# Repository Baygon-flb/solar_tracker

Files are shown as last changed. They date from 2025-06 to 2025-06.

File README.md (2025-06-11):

# solar_tracker
## Seguidor solar

Este projeto implementa um experimento de um seguidor que localiza uma fonte de luz e
mantém um sensor RGB apontado perpendicularmente para esta fonte, utilizando um arduíno Nano
como controlador. 

O objetivo é fazer a medição das intensidades dos componentes expectrais cromáticos RGB da luz 
solar ao longo de um dia, a partir do que é possível também calcular a temperatura de cor e a
intensidade total. 

Para essa medição é utilizado um módulo TCS34725 RGB Light Sensor.

O projeto conta com dois servos motores, um que controla a coordenada de altura e outro a 
coordenada de azimute do sensor, além de 4 LDR's, dispostos nas extremidades da placa de 
suporte do sensor, posicionados nos quadrantes presumidos como os pontos cardeais N,S,L e O. 

Com base na diferença de leitura dos LDR's, os motores são acionados, reposicionando a placa de
suporte do sensor, objetivando reorientar o conjunto até que haja convergência nos valores lidos 
dos LDR's (todos recebendo a mesma quantidade de luz), dentro de uma margem de erro estipulada, 
garantindo assim que o sensor estará, o máximo possível, apontado de forma perpendicular à fonte 
de luz. 

A leitura dos dados do sensor é realizada em um intervalo definido de tempo. Essas leituras são 
armazenadas na memória EEprom do arduíno e depois baixadas, via conexão serial, para um terminal, 
afim de que possam ser então capturados e tratados. Para controlar o intervalo de coleta dos 
dados do sensor é utilizado um módulo RTC (DS1307).

Os servos são controlados (sem uso de bilbioteca) através de uma rotina de timer interrupt, afim 
de garantir que não ocorrerão flickers ou jammers que comprometam a estabilidade da posição do 
sensor.

O detalhamento completo da elaboração e construção do projeto pode ser encontrado na pasta de 
documentação (pasta DOC).

Os componentes utilizados no projeto são:

* Arduino nano V3
* Módulo sensor TCS34725
* Módulo RTC DS1307
* Módulo StepDown DC/DC LM2596

As pastas do projeto são:
* CAD - Desenhos DWG dos componentes de montagem da caixa e suportes
* KICAD - Esquemático eletrônico e PCB
* INO - Arquivos de Sketch para a IDE do arduino
* STL - Arquivos para impressão das partes dos componentes de montagem
* DOC - Documentação do projeto

@baygon-flb

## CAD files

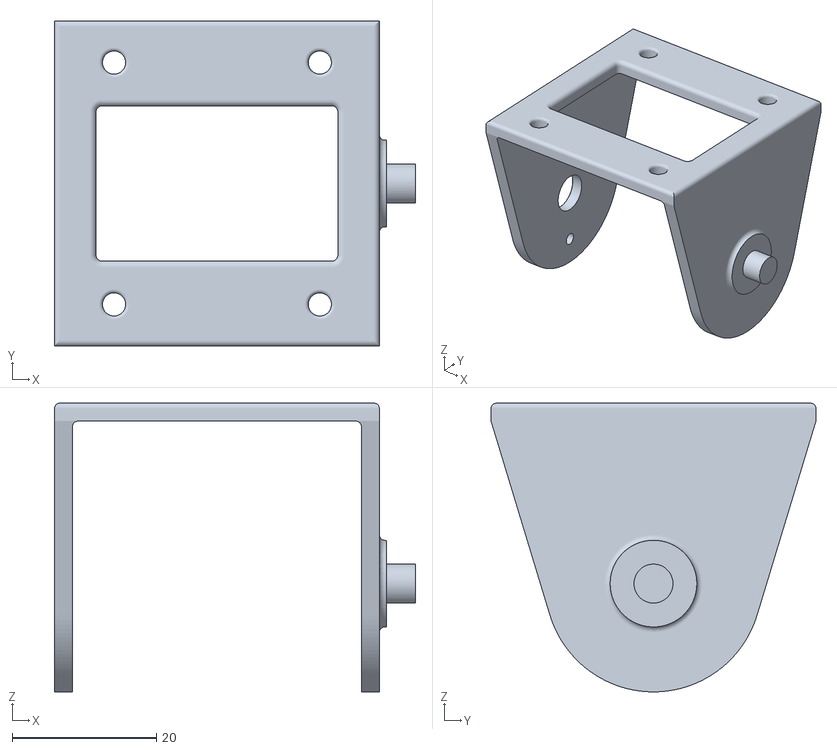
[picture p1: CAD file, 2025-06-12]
stl/suporte.stl
50.0 x 45.0 x 40.0

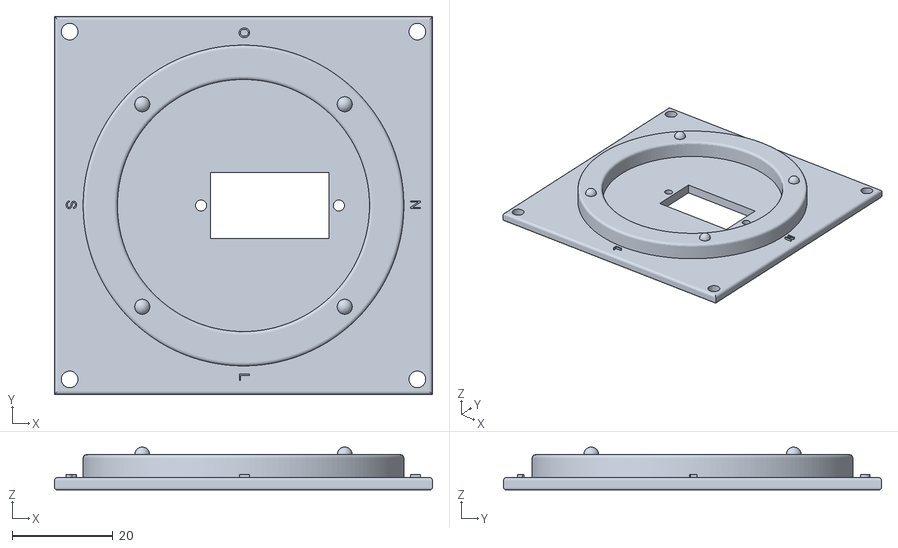
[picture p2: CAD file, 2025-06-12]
stl/tampa.stl
75.0 x 75.0 x 8.50

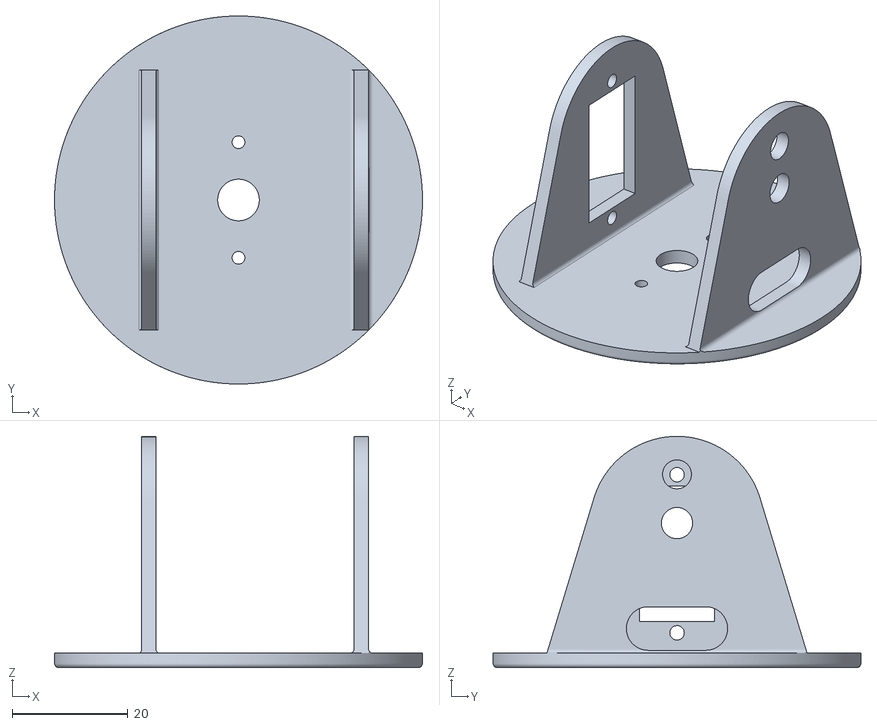
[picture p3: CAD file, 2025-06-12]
stl/base.stl
63.6 x 63.6 x 40.0

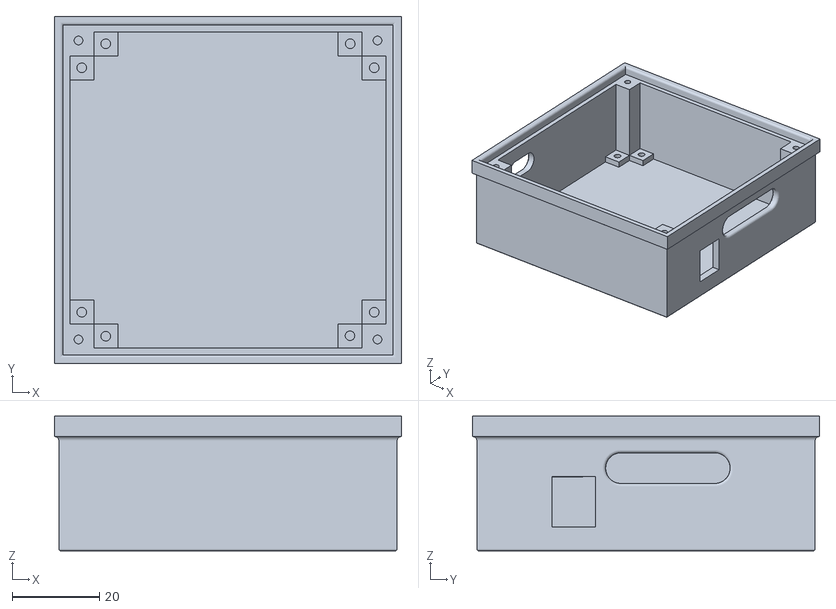
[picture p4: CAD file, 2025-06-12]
stl/caixa.stl
79.5 x 79.5 x 30.9

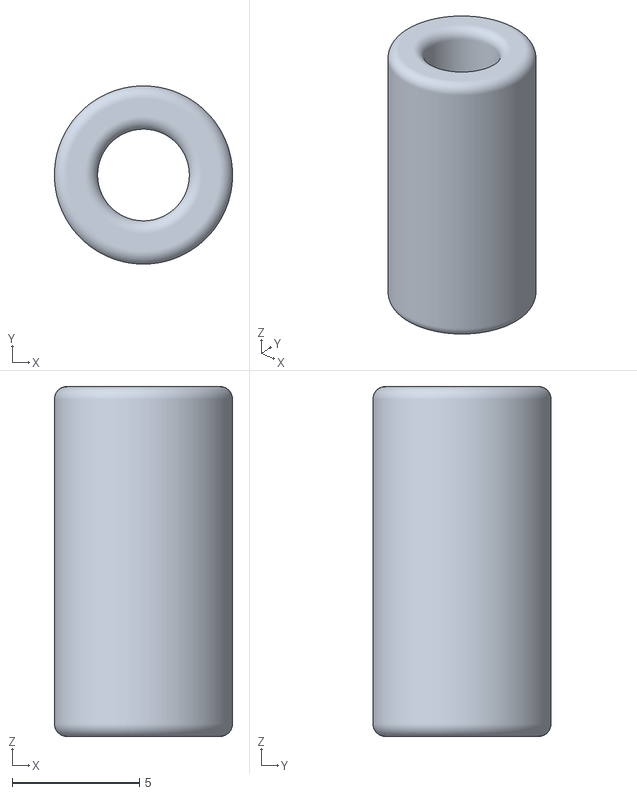
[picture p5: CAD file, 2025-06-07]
stl/espacador2.stl
7.00 x 7.00 x 13.8

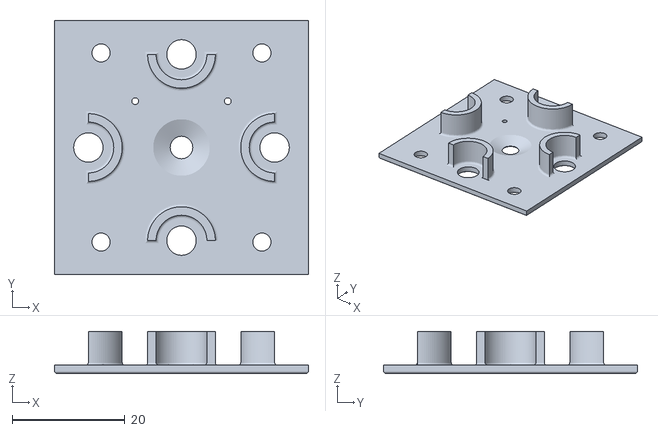
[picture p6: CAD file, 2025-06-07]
stl/pl_sensor.stl
45.0 x 45.0 x 7.50

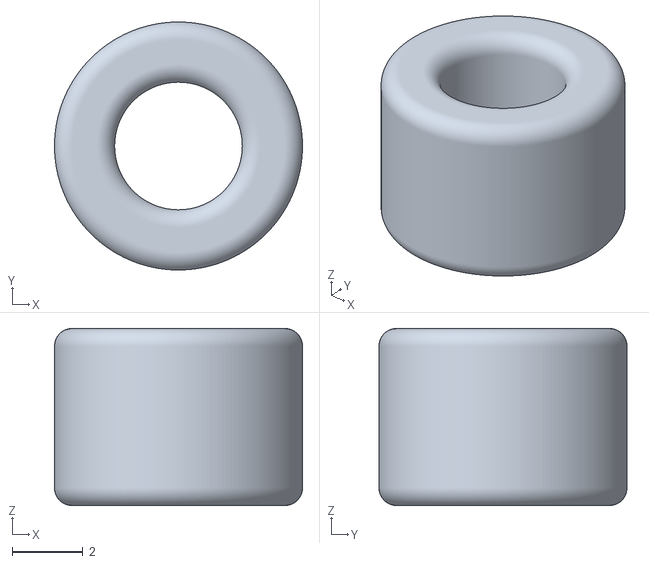
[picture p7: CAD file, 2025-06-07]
stl/espacador1.stl
7.00 x 7.00 x 5.00

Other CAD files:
cad/solar_tracker.dwg

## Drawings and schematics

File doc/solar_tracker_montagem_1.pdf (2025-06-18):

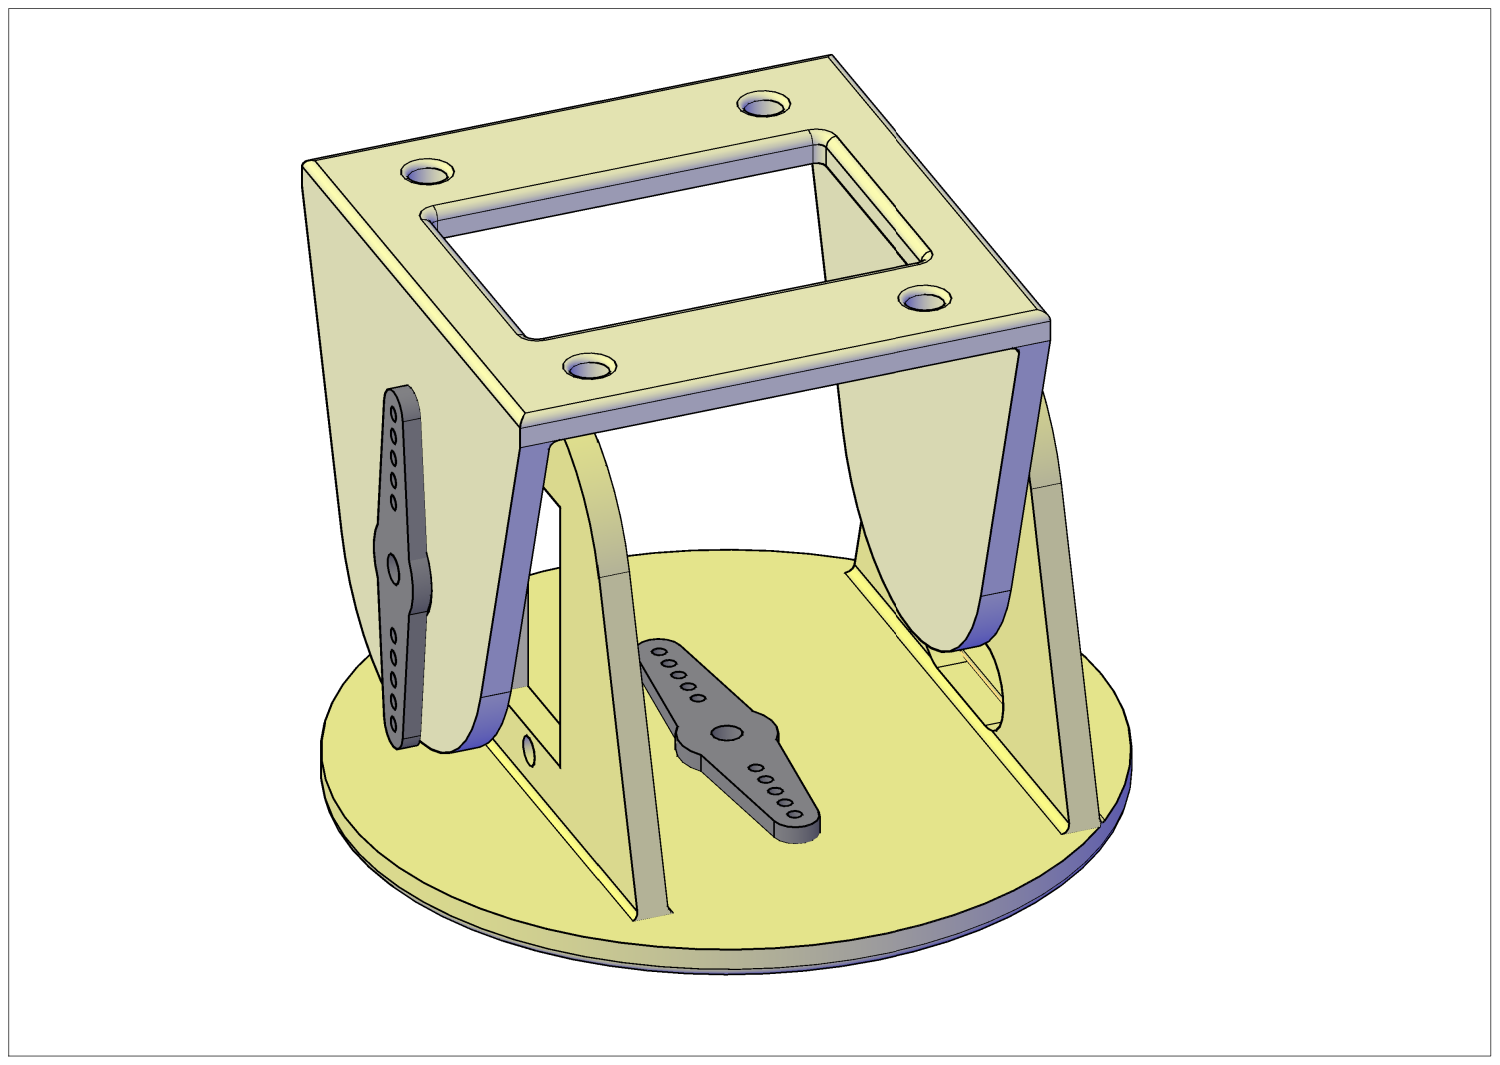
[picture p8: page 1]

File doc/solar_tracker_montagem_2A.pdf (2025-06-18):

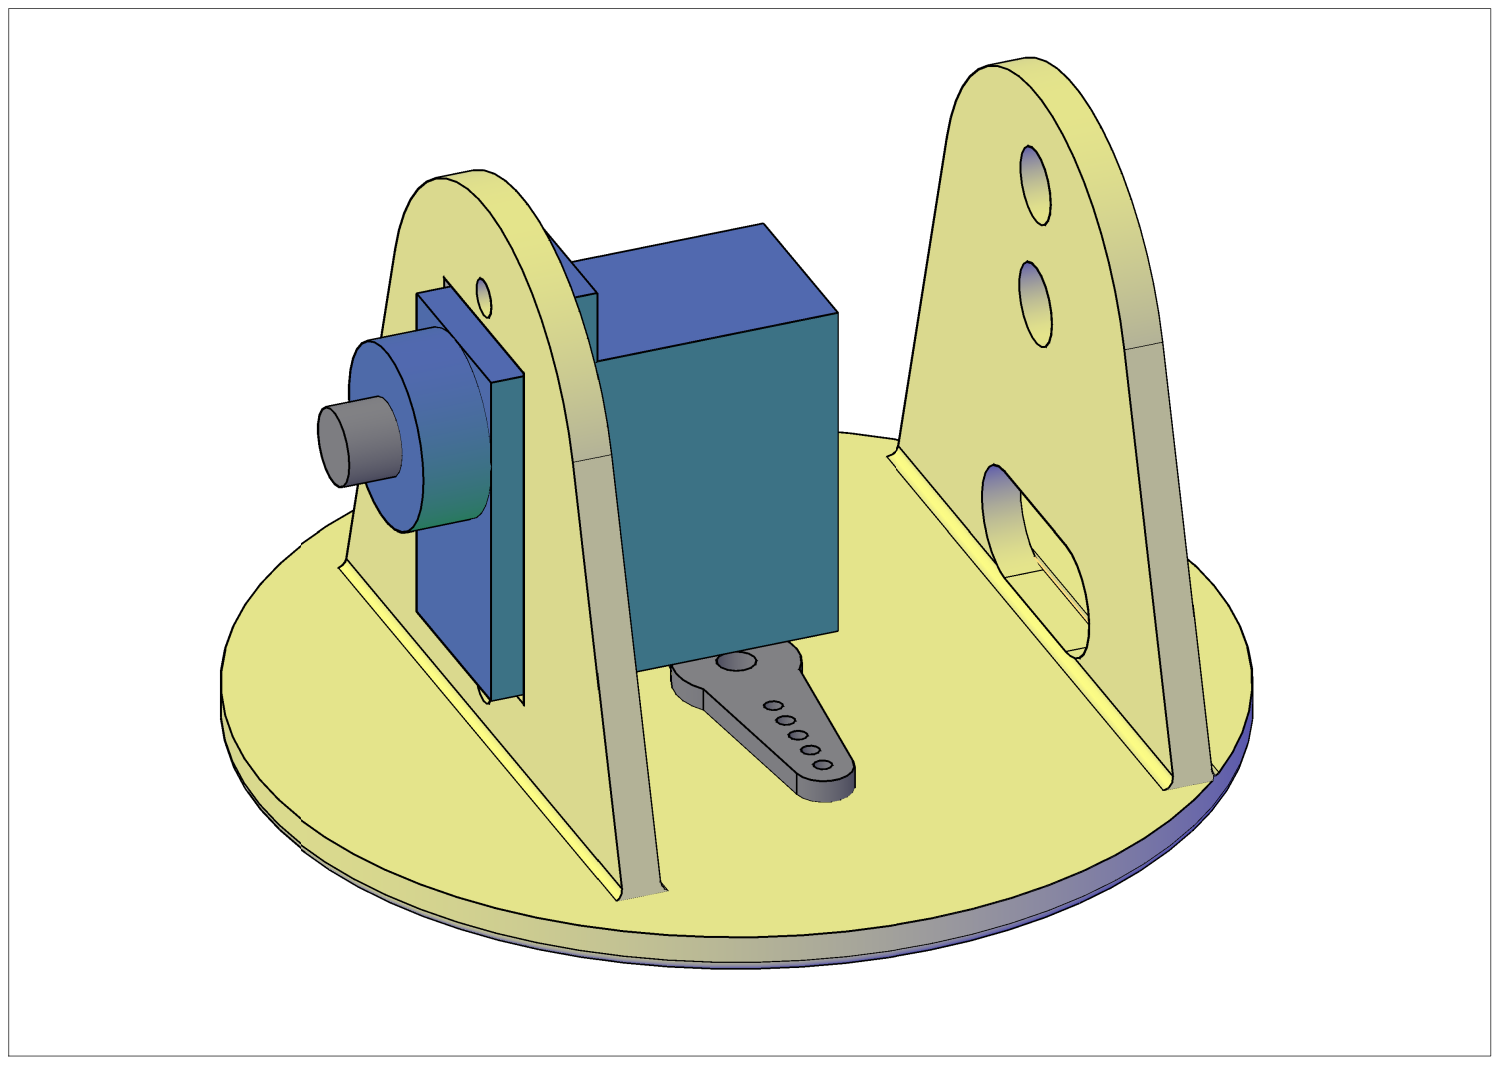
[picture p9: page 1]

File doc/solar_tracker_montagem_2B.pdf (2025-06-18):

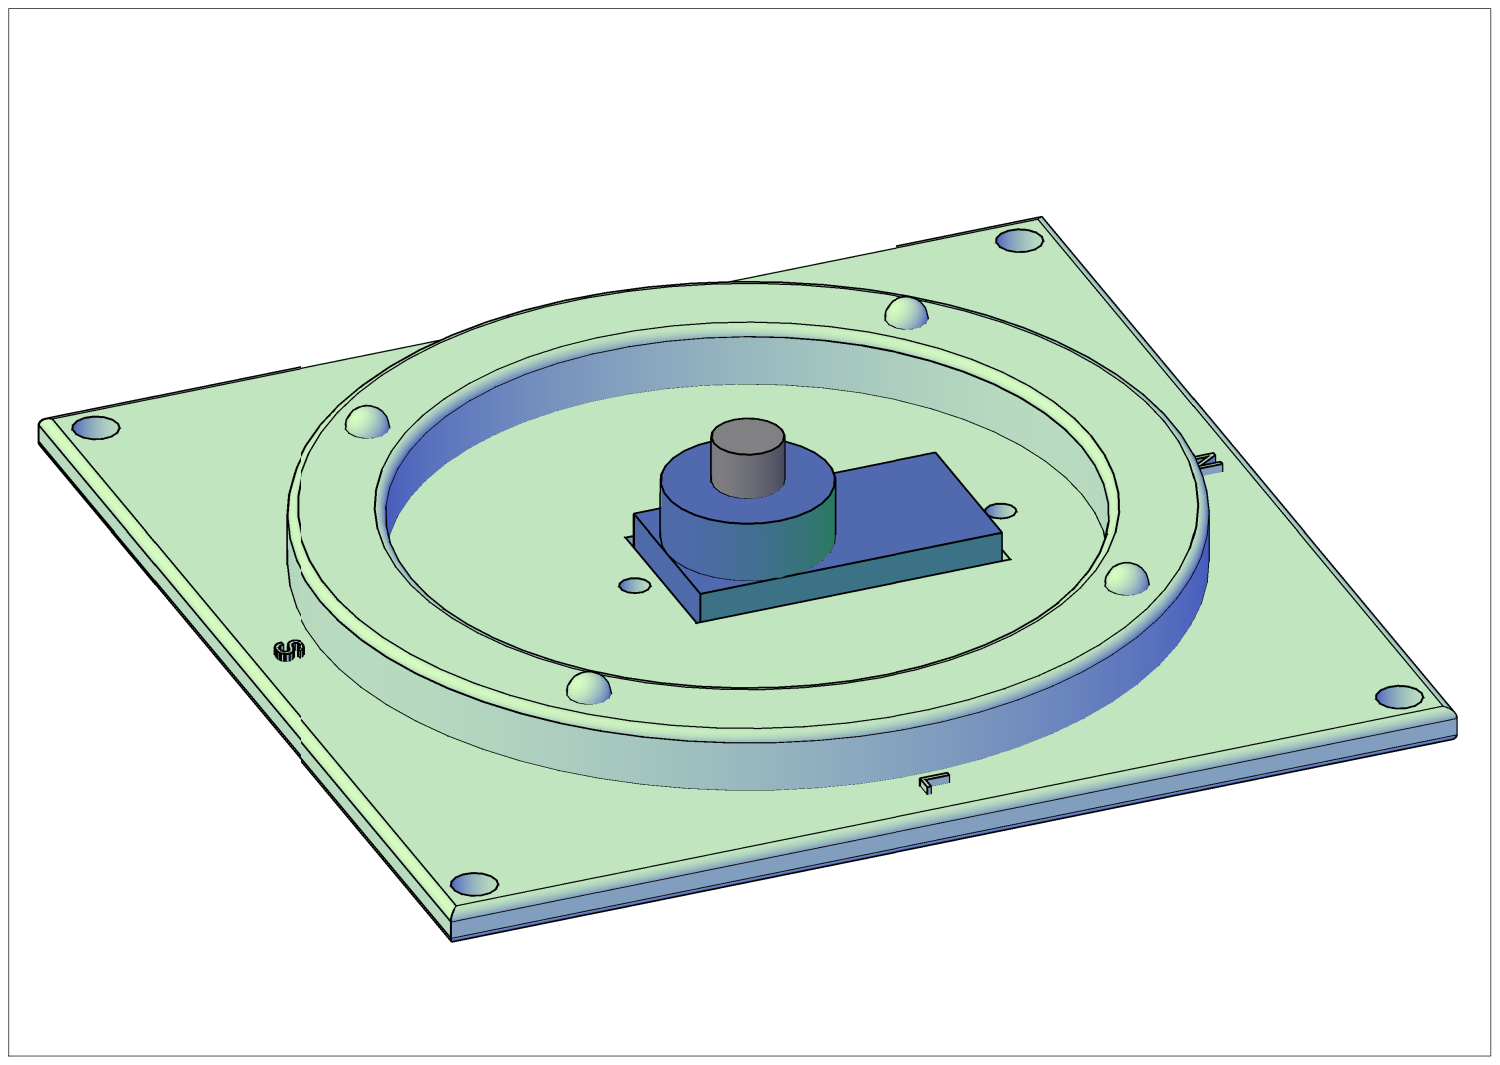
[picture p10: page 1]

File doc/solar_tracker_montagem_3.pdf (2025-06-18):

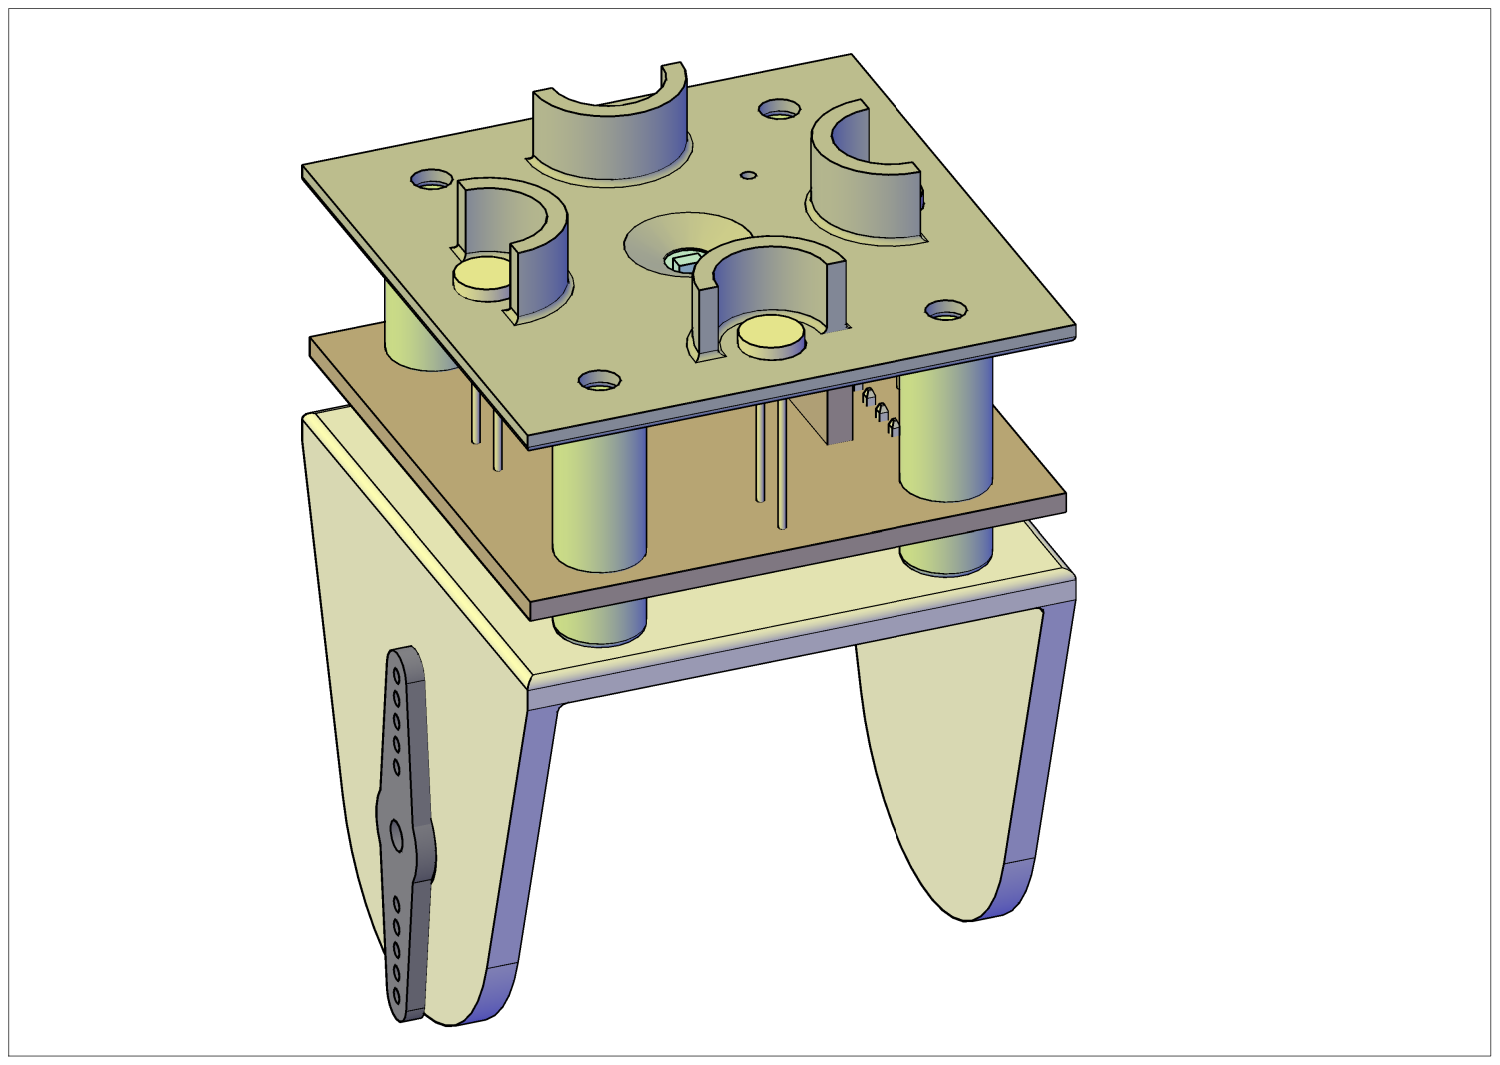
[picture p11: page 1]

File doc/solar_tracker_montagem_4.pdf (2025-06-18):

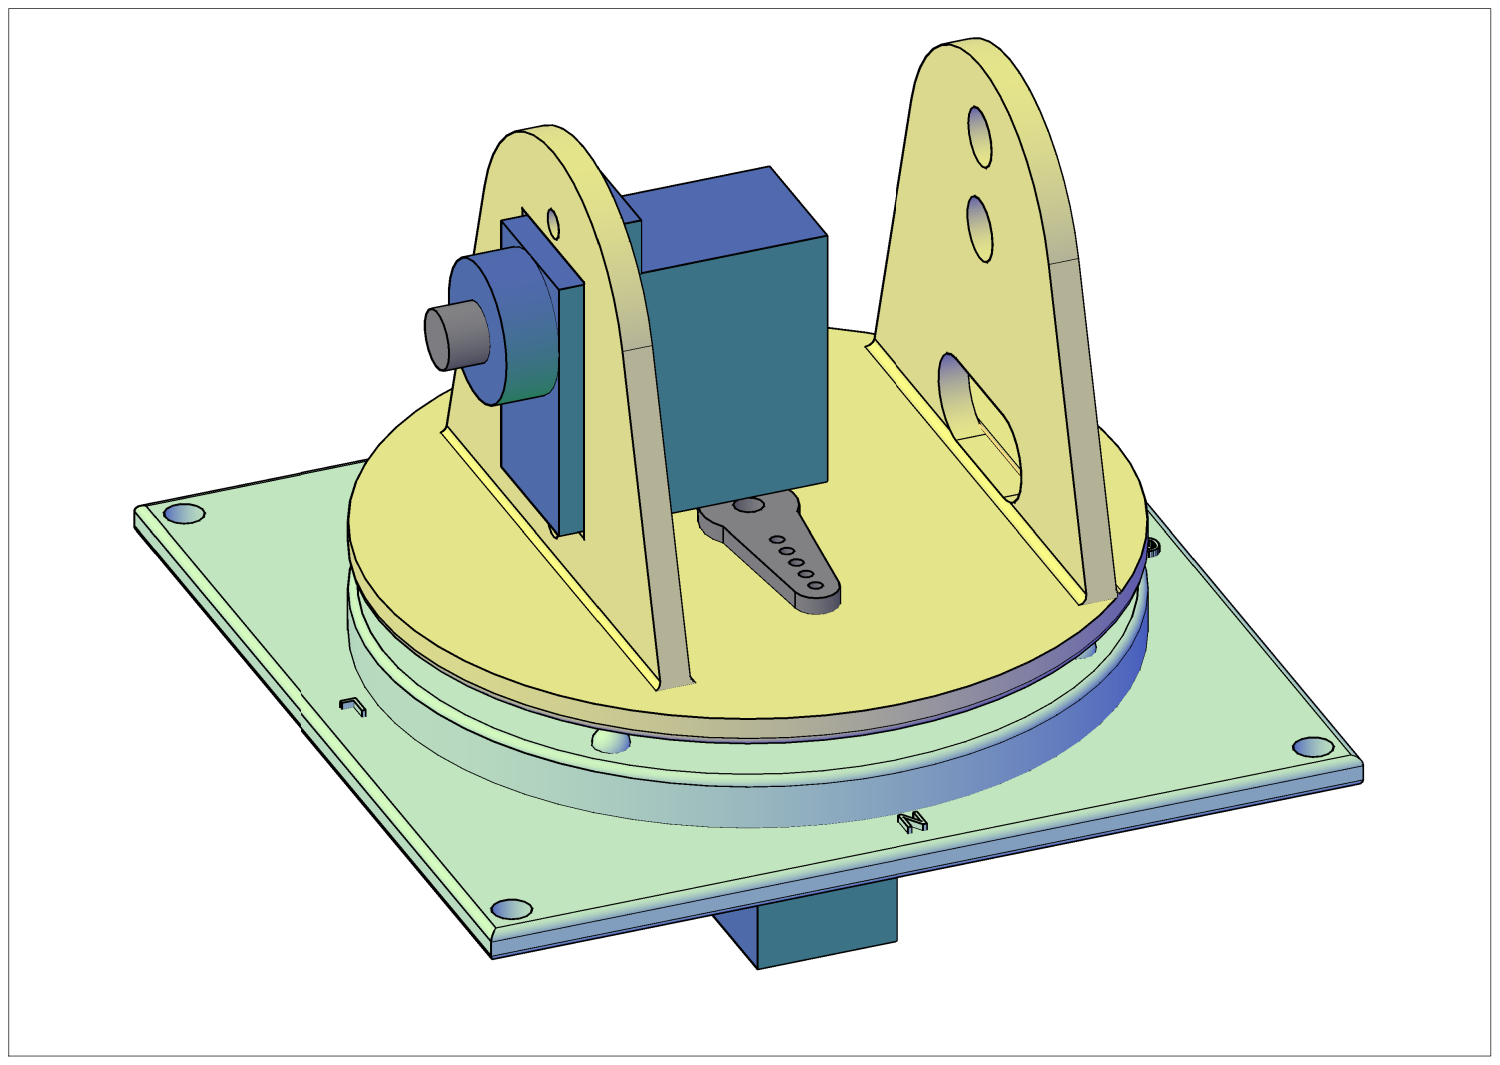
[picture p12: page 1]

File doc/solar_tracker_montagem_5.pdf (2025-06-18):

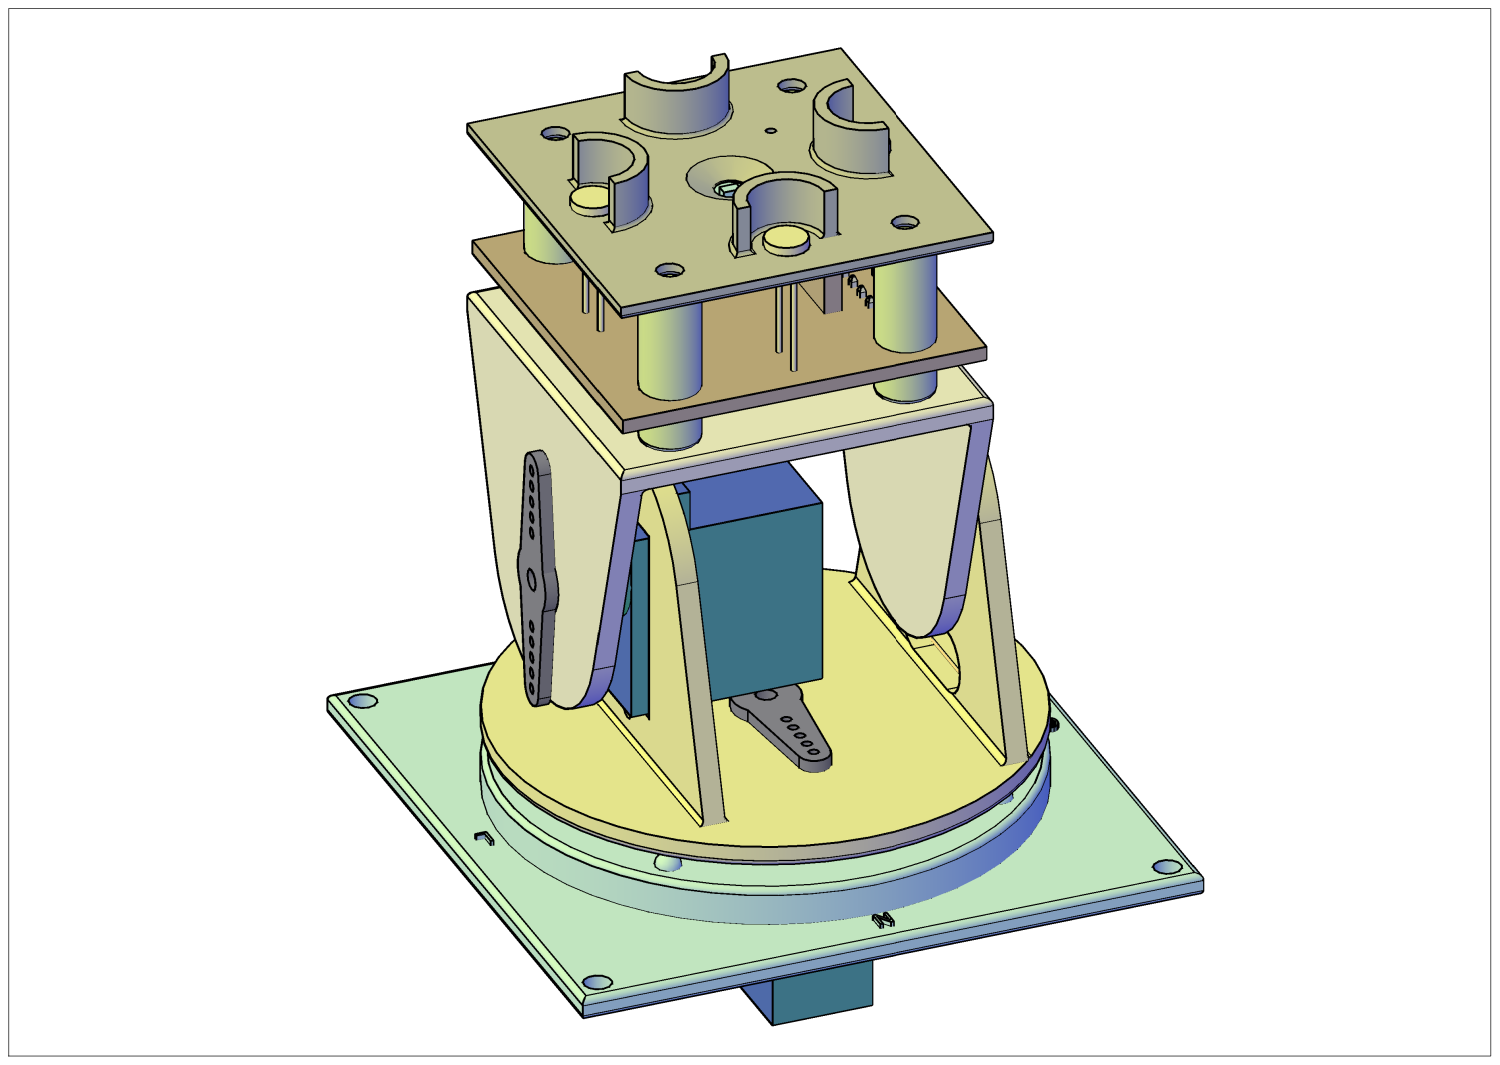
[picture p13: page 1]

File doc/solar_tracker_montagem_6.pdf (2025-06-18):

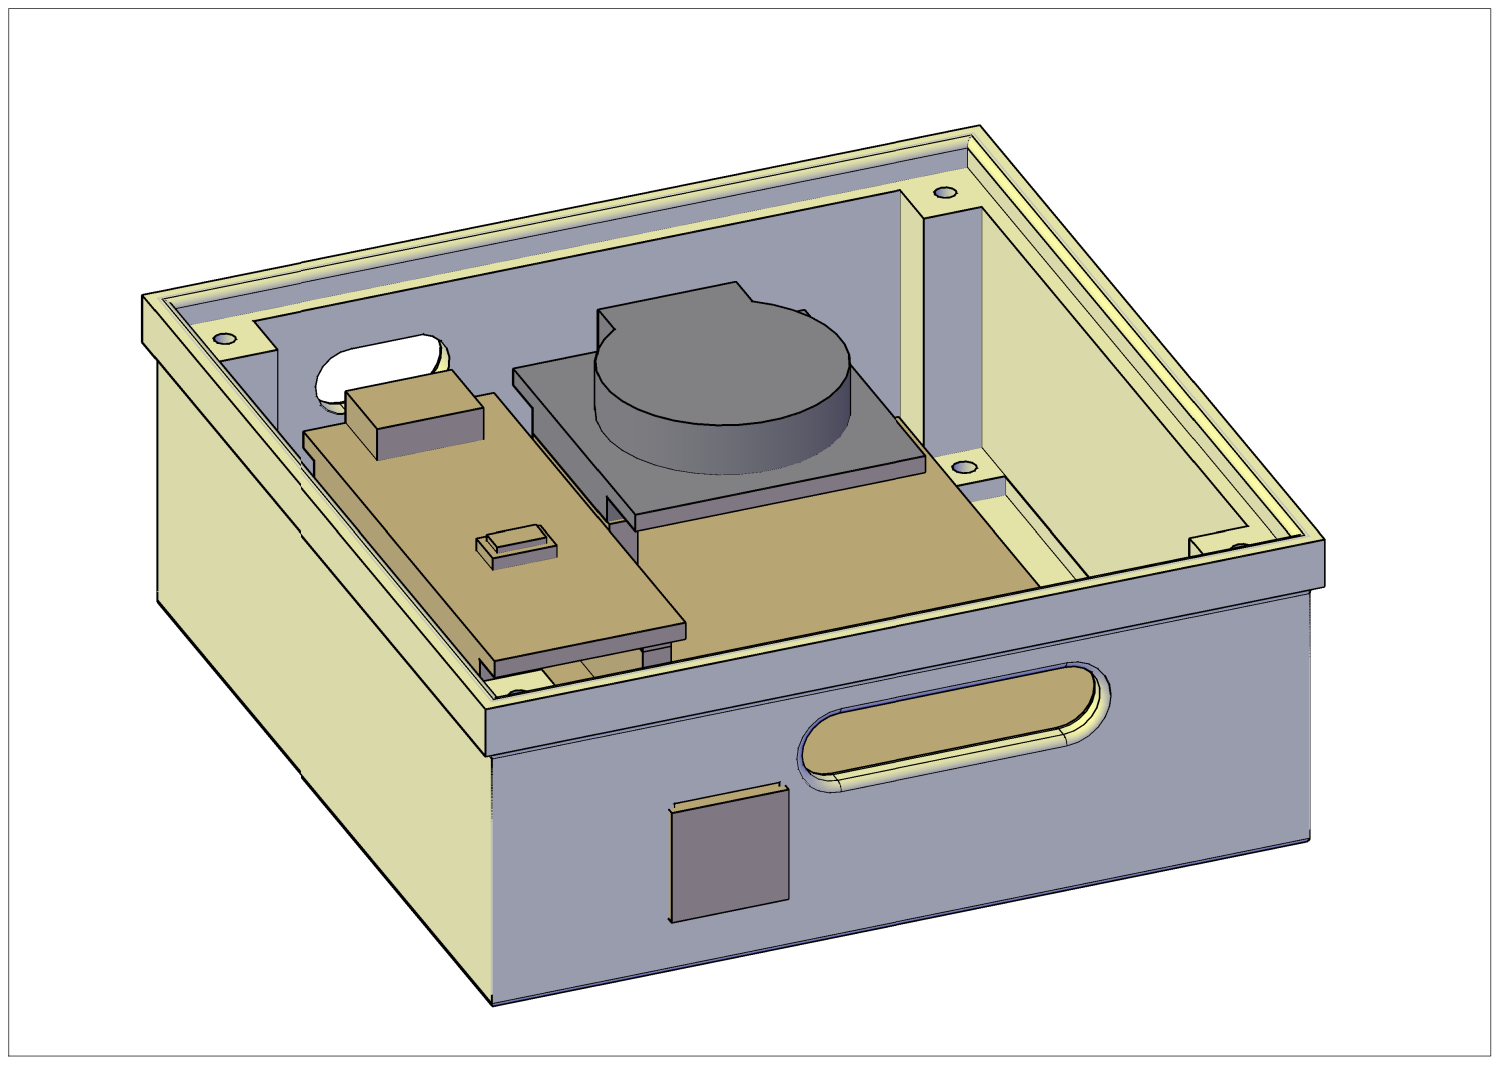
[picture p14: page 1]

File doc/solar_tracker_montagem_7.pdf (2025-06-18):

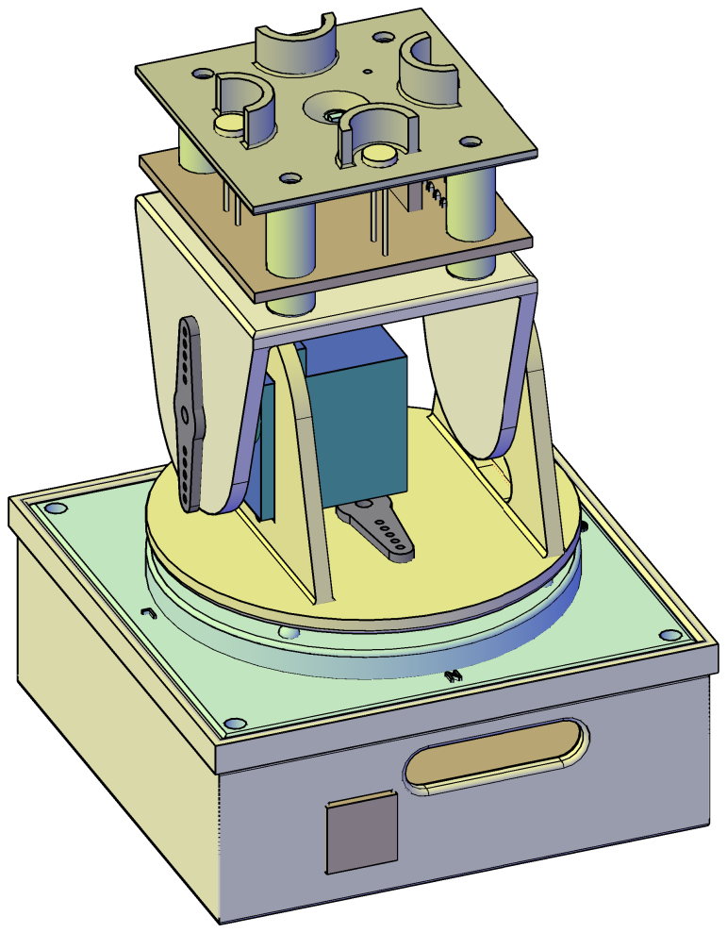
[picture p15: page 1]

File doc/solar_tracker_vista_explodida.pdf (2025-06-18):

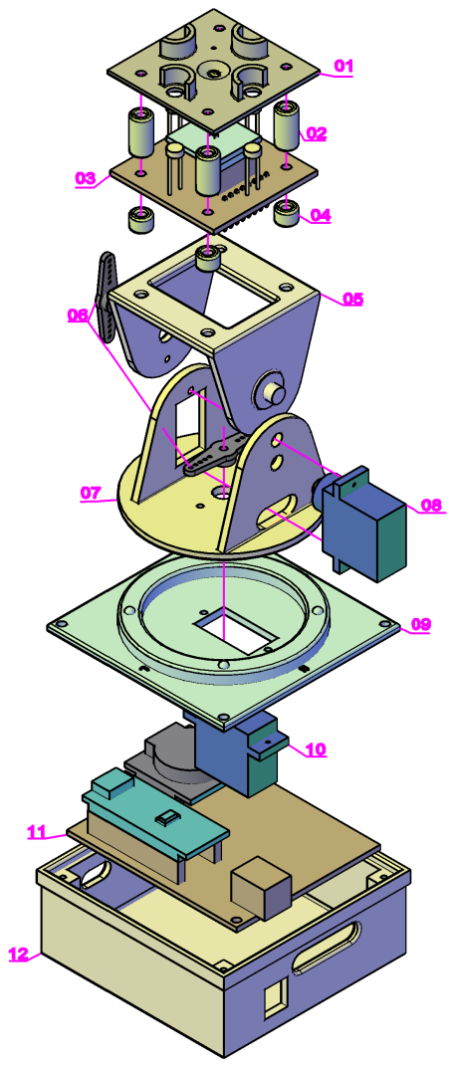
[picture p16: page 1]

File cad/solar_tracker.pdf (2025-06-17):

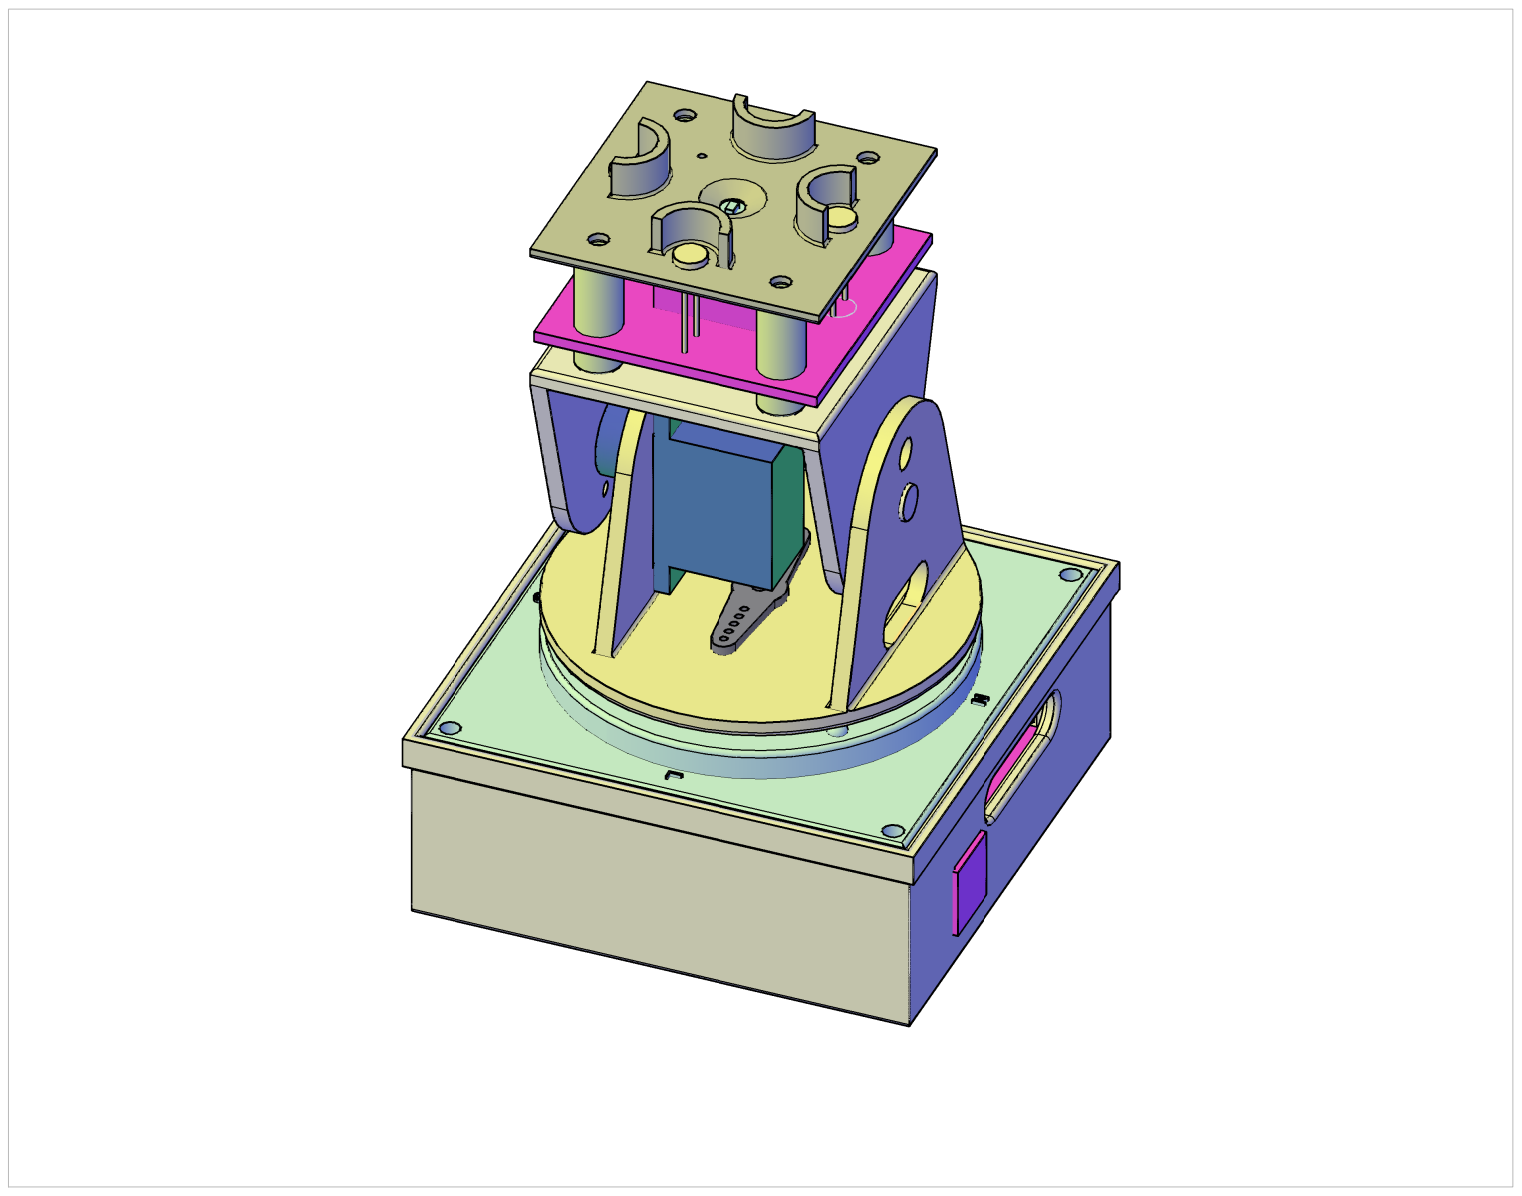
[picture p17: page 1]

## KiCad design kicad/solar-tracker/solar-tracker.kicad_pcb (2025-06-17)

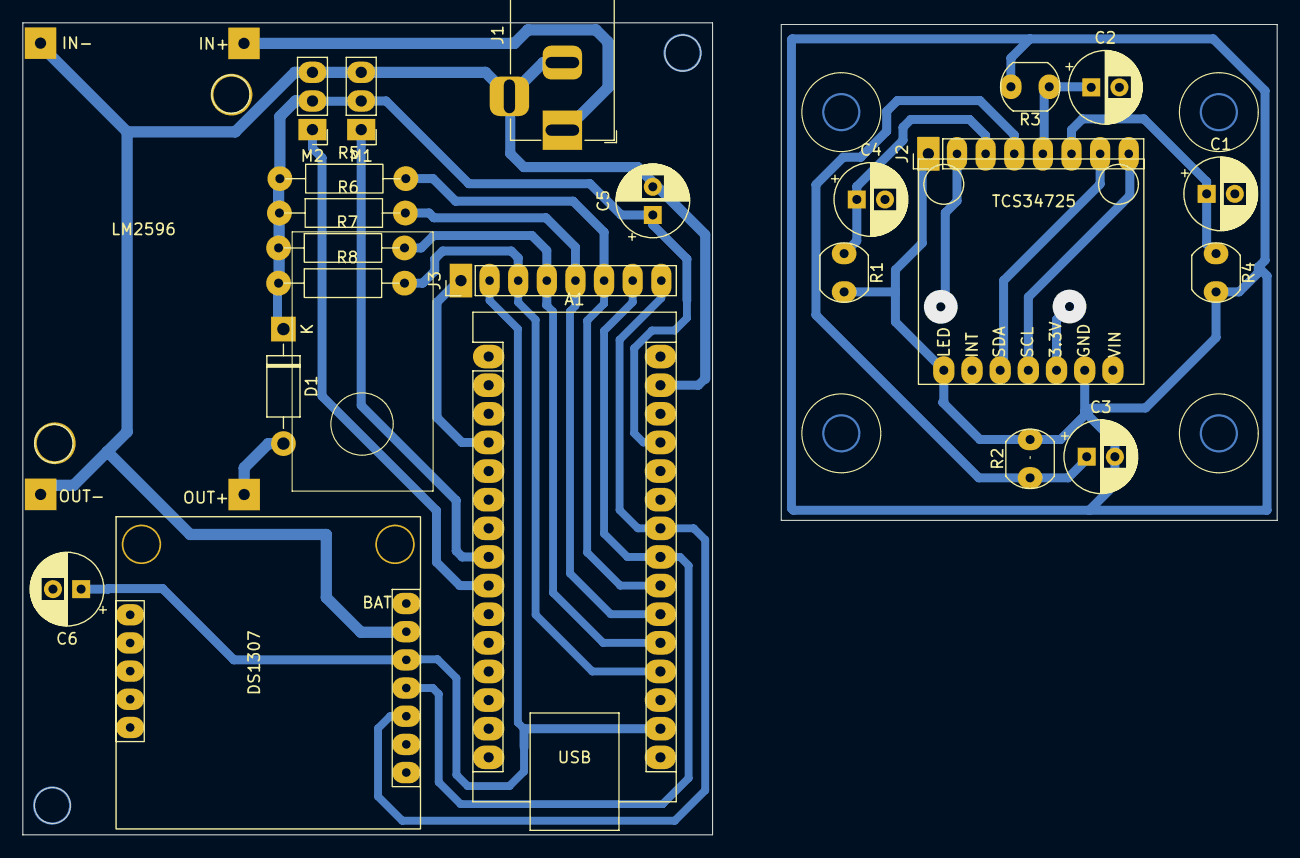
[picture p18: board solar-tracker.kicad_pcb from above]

Board: 2 copper layers, 111.3 x 72.0 mm, 24 parts (0 on the bottom side), 13 nets.

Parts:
A1: Arduino_Nano_v3.x; Arduino_Nano
C1, C2, C3, C4: 1uf; CP_Radial_D6.3mm_P2.50mm
C5, C6: 100UF; CP_Radial_D6.3mm_P2.50mm
D1: 1N4007; D_DO-41_SOD81_P10.16mm_Horizontal
DS1307: DS1307_RTC_MODULE
J1: Barrel_Jack_Switch; BarrelJack_Horizontal
J2, J3: Conn_01x08_Pin; PinHeader_1x08_P2.54mm_Vertical_large_pad
LM2596: LM2596_Step_Down_module
M1, M2: Motor_Servo; PinHeader_1x03_P2.54mm_Vertical
R1: LDR01; R_LDR_5.1x4.3mm_P3.4mm_Vertical
R2: LDR02; R_LDR_5.1x4.3mm_P3.4mm_Vertical
R3: LDR03; R_LDR_5.1x4.3mm_P3.4mm_Vertical
R4: LDR04; R_LDR_5.1x4.3mm_P3.4mm_Vertical
R5, R6, R7, R8: R; resistor_250mw_12mm
TCS34725: TSC34725_RGB_SENSOR

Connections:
+3V3: A1.17 (3V3), C6.1, DS1307.3 (VCC), J2.2, J3.2, TCS34725.5 (3.3V)
+5V: A1.27 (+5V), C5.1, D1.1 (K), M1.2 (+), M2.2 (+), R5.1, R6.1, R7.1, R8.1
/Placa_sensor/LDR1: A1.19 (A0), C4.1, J2.3, J3.3, R1.1, R8.2
/Placa_sensor/LDR2: A1.20 (A1), C3.1, J2.4, J3.4, R2.1, R7.2
/Placa_sensor/LDR3: A1.21 (A2), C2.1, J2.5, J3.5, R3.1, R6.2
/Placa_sensor/LDR4: A1.22 (A3), C1.1, J2.6, J3.6, R4.1, R5.2
/Placa_sensor/SCL: A1.24 (A5), DS1307.5 (SCL), J2.8, J3.8, TCS34725.4 (SCL)
/Placa_sensor/SDA: A1.23 (A4), DS1307.4 (SDA), J2.7, J3.7, TCS34725.3 (SDA)
GND: A1.4 (GND), A1.29 (GND), C1.2, C2.2, C3.2, C4.2, C5.2, C6.2, DS1307.2 (GND), J1.2, J1.3, J2.1, J3.1, LM2596.2 (IN-), LM2596.4 (OUT-), M1.3 (-), M2.3 (-), R1.2, R2.2, R3.2, R4.2, TCS34725.1 (LED), TCS34725.6 (GND)
unnamed: A1.8 (D5), M1.1 (PWM)
unnamed: A1.9 (D6), M2.1 (PWM)
unnamed: D1.2 (A), LM2596.3 (OUT+)
VDD: J1.1, LM2596.1 (IN+)

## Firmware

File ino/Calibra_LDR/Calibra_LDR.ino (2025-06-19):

//Calibra_LDR

#define PIN_N A0 //LDR1 leste 
#define PIN_O A1 //LDR2 Norte
#define PIN_L A2 //LDR3 Sul
#define PIN_S A3 //LDR4 oeste
#define SERIAL_RATE 115200

long tempo = 0;

void setup() {
  Serial.begin( SERIAL_RATE );
  // Configurando os LDRS
  pinMode( PIN_L, INPUT_PULLUP );    
  pinMode( PIN_N, INPUT_PULLUP );
  pinMode( PIN_S, INPUT_PULLUP );
  pinMode( PIN_O, INPUT_PULLUP );

  Serial.println(F("---------------"));
  Serial.println("offset dos LDR's");
  Serial.println( " N     S     L     O ");

}

void loop() {
  if ( abs( millis()-tempo) > 1000 ) { 
    float L=0, N=0, S=0, O=0;
    for ( int i=1; i<10; i++ ) {
      L += analogRead( PIN_L );
      N += analogRead( PIN_N );
      S += analogRead( PIN_S );
      O += analogRead( PIN_O );
    }
    L = L/10;
    N = N/10;
    S = S/10;
    O = O/10;

    float offset_N = (( S - N )/2)/N;
    float offset_S = (( N - S )/2)/S;
    float offset_L = (( O - L )/2)/L;
    float offset_O = (( L - O )/2)/O;
    
    Serial.print( offset_N );
    Serial.print("  ");
    Serial.print( offset_S );
    Serial.print("  ");
    Serial.print( offset_L );
    Serial.print("  ");
    Serial.println( offset_O );

    tempo = millis();
  }
  delay(100);
}

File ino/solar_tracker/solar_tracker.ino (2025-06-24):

// Solar_tracker
// Seguidor solar
// Este projeto implementa um seguidor solar com 2 eixos, que rastreia, posiciona e mantém um sensor apontado
// perpendicularmente ao sol (ou outra fonte de luz), de forma a garantir a incidência máxima da intensidade 
// luminosa sobre o sensor. Neste caso específico, o sensor utilizado é para medir a variação do espectro, 
// intensidade e a temperatura da luz emitida pela fonte, utilizando um módulo sensor RGB TCS34725. 
// O projeto conta ainda com um relógio RTC, que permite controlar o horário de coleta dos 
// parâmetros de medição. As medições são tomadas a cada 10 minutos, à partir do horário definido como
// alvorada, até o horário definido como crepúsculo, armazenando os dados coletados na EEPROM.
// Se conectada a serial, o projeto entra no modo de ajuste de parâmetros e descarga dos dados coletados
// 

#include <Arduino.h>
#include <SPI.h>
#include <Wire.h>
#include <Adafruit_TCS34725.h>
#include <RTClib.h>  //Adafruit RTClib
#include <avr/wdt.h>
#include "regdata.h"
#include "srvctrl.h"

#define PIN_S1 5
#define PIN_S2 6
#define PIN_N A0 //LDR1 leste 
#define PIN_O A1 //LDR2 Norte
#define PIN_L A2 //LDR3 Sul
#define PIN_S A3 //LDR4 oeste
#define SERIAL_RATE 115200
#define DEBUG 0

//Instanciando as classes
Adafruit_TCS34725 TCS = Adafruit_TCS34725(TCS34725_INTEGRATIONTIME_300MS, TCS34725_GAIN_1X);
RTC_DS1307 rtc;
Srvctrl s1( PIN_S1 ); //altura
Srvctrl s2( PIN_S2 ); //azimute

// variáveis de controle
float minuto = 0;
float hora = 0;
long tempo = 0;
int erro = 3;
float tolerancia = (2.55*erro);
float intervalo = 1;

//horarios de inicio e fim
float hora_inicio = 5;
float minuto_inicio=30;
float hora_fim = 22;
float minuto_fim=30;
float inicio = hora_inicio+(minuto_inicio/60);
float fim = hora_fim+(minuto_fim/60);

//controle dos servos
int azimuteMin = 15;
int azimuteMax = 175;
int alturaMin = 10;
int alturaMax = 175;
int S2angulo = int((azimuteMax-azimuteMin)/2);
int S1angulo = int((alturaMax-alturaMin)/2);

//Calibragem LDR's
float offset_N = 0.043;
float offset_S = -0.04;
float offset_L = -0.06;
float offset_O = 0.07;

//Configuracao do registro de dados
// O formato do registro de dados é  
// Para resoluçao de 8 bits por canal de cor: 
// [ hora - 1 byte ][ minuto - 1 byte][ Red - 1 byte][ green - 1 byte][ blue - 1 byte] = 5 bytes
// Capacidade de memória para cerca de 400 registros
// 
// Para resoluçao de 16 bits por canal de cor: 
// [ hora - 1 byte ][ minuto - 1 byte][ Red - 2 bytes][ green - 2 bytes][ blue - 1 bytes] = 8 bytes
// Capacidade de memória para cerca de 250 registros
//
int resolucao = 2; //Resolução em bytes do registro de dados do sensor
int lenReg = 2+(4*resolucao); //tamanho do registro de dados
int reserva = 10; //numero de bytes para serem reservados no inicio da memória
Regdata reg(lenReg, reserva);

void debug( String msg, bool nl = true ) {

  if( Serial && DEBUG ) {
    if (nl) { Serial.println( msg ); }
    else { Serial.print( msg ); }
  }
} 

// Rotina de interrupção do timer
ISR(TIMER2_OVF_vect) {//trata Overflow do Timer,
  //Executa a cada 1ms aproximadamente  
  s1.pulse();
  s2.pulse();
} //end Timer2 OVF

// Envia as dados das amostras para o terminal serial
void descarrega(){
  wdt_reset();
  Serial.println();
  Serial.println(F("Descarregando os dados da memoria..") );
  Serial.println();
  for( int p=0; p < reg.curAddr(); p++) {
    int data[ lenReg ];
    reg.read( p, data );
    if( resolucao == 2 ){
      data[2] = data[2]*255+data[3];
      data[3] = data[4]*255+data[5];
      data[4] = data[6]*255+data[7];
    }
    for( int i=0; i<5; i++) {
      Serial.print( data[i] );
      Serial.print(";");
    }
    Serial.println();
  }
  reg.reset();
}

void config( ) {

  DateTime now = rtc.now();
  Serial.println(F("---------------"));
  Serial.println(F("DEBUG"));
  Serial.println("Hora atual: "+String( now.hour())+":"+String(now.minute()));
  Serial.println("var minuto: "+String( int( minuto )));
  Serial.println("Memoria Eprom livre: "+String( reg.free()));
  Serial.println("Slot de memória atual: "+String( reg.curAddr()));
  Serial.println("LDR's");
  Serial.println("LDR1 (N): "+String( int( analogRead( PIN_N )+offset_N)));
  Serial.println("LDR2 (O): "+String( int( analogRead( PIN_O )+offset_O)));
  Serial.println("LDR3 (L): "+String( int( analogRead( PIN_L )+offset_L)));
  Serial.println("LDR4 (S): "+String( int( analogRead( PIN_S )+offset_S)));
  Serial.println("Servos:");
  Serial.println("Azimute: "+String( int(s2.getTarget())));
  Serial.println("Altura: "+String( int(s1.getTarget())));
  Serial.println();
}

void setup() {
  // coloca sensor TCS34725 em hibernação
  //TCS.disable();

  reg.recover(); // recupera a posicao de memoria anterior

  //habilita o whatchdog para 5s
  wdt_enable(WDTO_4S);

  Serial.begin( SERIAL_RATE );
  Serial.println(F("SOLAR TRACKER"));
  Serial.println(F("-------------"));
  
  Serial.println(F("Inicializando o RTC..."));
  while(!rtc.begin()) { delay(50); }
  wdt_reset();
  if (! rtc.isrunning() ) {
    Serial.println(F("RTC não inicializado. Ajustando horário"));
    rtc.adjust(DateTime(F(__DATE__), F(__TIME__)));
  }

  DateTime now = rtc.now();
  minuto = int(now.minute()/intervalo)*intervalo;
  hora = now.hour();

  Serial.println( "Hora atual: "+String( now.hour())+":"+String( now.minute()));
  
  Serial.println(F("Inicializando LDRs..."));
  // Configurando os LDRS
  pinMode( PIN_L, INPUT_PULLUP );    
  pinMode( PIN_N, INPUT_PULLUP );
  pinMode( PIN_S, INPUT_PULLUP );
  pinMode( PIN_O, INPUT_PULLUP );

  Serial.println(F("Inicializando Servos..."));
  //configura os servos
  s1.setAnguloMax(azimuteMax);
  s1.setAnguloMin(azimuteMin);
  s1.setDutyMax( int( 200/18*azimuteMax+400) );
  s1.setDutyMin( int( 200/18*azimuteMin+400) );
  s1.setTarget( S1angulo );
  s2.setAnguloMax(alturaMax);
  s2.setAnguloMin(alturaMin);
  s2.setDutyMax( int( 200/18*alturaMax+400) );
  s2.setDutyMin( int( 200/18*alturaMin+400) );
  s2.setTarget( S2angulo );

  s1.start();
  s2.start();

  Serial.println(F("Inicializando o timer..."));
  //configura o timer interrupt para enviar o sinal de controle dos servos
  TCCR2A = 0xA3;                                        //pwm não invertido, fast pwm 
  TCCR2B = 0x04;                                        //pre scaler 1:64
  TIMSK2 = 0x01;                                        //liga interrupção do Timer2
  sei();                                                //habilita interrupção global

  Serial.println(F("Tudo pronto!"));
  Serial.println(F("Aperte C para entrar no modo de configuração"));
  Serial.println(F("Aperte D para descarregar dados da memória"));
  Serial.println();

  //minuto = minuto_inicio;
  //hora = hora_inicio;
  
}

void loop() {
  wdt_reset();
  
  // Faz 10 medições dos valores dos LDR's e calcula a média
  float L=0, N=0, S=0, O=0;
  for ( int i=1; i<10; i++ ) {
    L += analogRead( PIN_L );
    N += analogRead( PIN_N );
    S += analogRead( PIN_S );
    O += analogRead( PIN_O );
  }
  L = L/10+(L/10*offset_L);
  N = N/10+(N/10*offset_N);
  S = S/10+(S/10*offset_S);
  O = O/10+(O/10*offset_O);

  float k=0.1; // Coeficiente proporcional

  // Ajuste do angulo de azimute
  if( abs( L - O ) > tolerancia) {
    S2angulo -= int(k*( L - O ));
  }
  
  //Ajuste do angulo de altura
  if( abs( N - S ) > tolerancia) {
    S1angulo -= int(k*( N - S ));
  }
  
  if( S1angulo > azimuteMax ) { S1angulo = azimuteMax; }
  if( S1angulo < azimuteMin ) { S1angulo = azimuteMin; }
  if( S2angulo > alturaMax ) { S2angulo = alturaMax; }
  if( S2angulo < alturaMin ) { S2angulo = alturaMin; }

  // Envia os novos angulos para os Servos
  s1.setTarget( S1angulo );
  s2.setTarget( S2angulo );

  // Controle do tempo de coleta de dados
  float agora, m;
  DateTime now;
  if ( abs( millis()-tempo) > 5000 ) { 
    now = rtc.now();
    hora=now.hour();
    m = now.minute();
    agora = hora+( m/60);
    tempo = millis();
  }

  //Se estiver no intervalo de amostragem, faz leitura e salva na memória.
  if ( agora >= inicio && agora <= fim && ( int(m)%int(intervalo))==0 && m != minuto ) {
    minuto=m;
    //Lendo TSC34725
    uint16_t r=0, g=0, b=0, c=0;
    while ( true ) {
      if( resolucao == 1 ){
        float r=0, g=0, b=0;
        TCS.getRGB( &r, &g, &b);
      }  
      else { 
        TCS.getRawData( &r, &g, &b, &c ); 
      }     
      if( !((r+g+b+c)==0) ) { break; }
      Serial.println( "Erro na leitura do sensor");
      TCS.disable();
      delay( 1000 );
      TCS.enable();      
    }
    wdt_reset();
  
    uint8_t data[ lenReg ];
    data[0] = uint8_t( hora );
    data[1] = uint8_t( minuto );
    if( resolucao == 1 ){
      data[2] = uint8_t( r );
      data[3] = uint8_t( g );
      data[4] = uint8_t( b );
    } else {
      data[2] = uint8_t( r/255 );
      data[3] = uint8_t( r - (data[2]*255));
      data[4] = uint8_t( g/255 );
      data[5] = uint8_t( g - (data[4]*255));
      data[6] = uint8_t( b/255 );
      data[7] = uint8_t( b - (data[6]*255));
    }
    
    //Registra amostragem na EEprom
    reg.write( data );

    String msg = "";
    msg+=String(int(hora))+":"+String(int(minuto));
    msg+=" | R: "+String(r)+" | G: "+String(g)+" | B: "+String(b);
  
    Serial.println( msg );

  }
  delay( 30 ); 
  char input = Serial.read();
  if ( String(input)=="D"){ descarrega(); }
  if ( String(input)=="C"){ config(); }
  if ( String(input)=="R"){
    Serial.println( "R para sair..");
    s1.setTarget(90);
    s2.setTarget(90);
    while( Serial.read() != "R"){ delay(30);}
  }
 
}

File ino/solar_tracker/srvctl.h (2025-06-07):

// Classe de controle de servo motor
// Esta classe controla o reposicionamento um servo motor, para que o movimento aconteça de forma gradual (smooth).
//
// Inicializacao: svctrl servoObj( pino_saida ) 
// Metodos:   
// srvctrl( int pin ) = Instancia um objeto de controle do servo ligado no pino informado
// setTarget( int angulo ) = Move o servo para o angulo duty ( 0 - 180 ) ou a velocidade e sentido de rotação, se o servo for 360o
// getTarget() = Retorna o duty atual do servo 
// getDuty() = Retorna a largura de pulso do alvo atual
// pulse() = Envia pulso de controle para o servo
// step() = Reposiciona o servo conforme avançando/retrocendendo o angulo definido por pace
// stable() = Retorna verdadeiro se o servo estiver posicionado no angulo definido como alvo
// setPace( int passo ) = Define o pace para o valor informado em passo
// setDutyMin( int pulso ) = Define a largura de pulso (em ms) para o angulo mínimo do servo
// setDutyMax( int pulso ) = Define a largura de pulso (em ms) para o angulo máximo do servo
// setAnguloMin = Define o angulo mínimo do servo
// setAnguloMax = Define o angulo máximo do servo
// getAnguloMin = Define o angulo mínimo do servo
// getAnguloMax = Define o angulo máximo do servo
// setSync( long tempo ) = Define o tempo de sincronia do servo (intervalo de tempo para envio do pulso de controle)
// getSync() = Retorna o tempo de sincronia do servo
// stop() = Desliga o servo
// start() = Liga o servo e posiciona no último angulo definido como alvo
//
// Os valores definidos por padrão na classe atendem as especificações de micro servos do tipo Futaba de 180o modelos SG90 e MG995;
//
// Para evitar o flicker dos servos, faremos o controle do tempo de pulso dos servos através do interrupt do timer 2 do arduino
// 
// A base de tempo:
//
// O Timer 2 será ajustado para um pre scaler de 1:64 (fast pwm). Por padrão, o pre scaler é de 1024.
// A resolução do timer 2 é de 256 (8 bits).
// O ciclo de máquina do arduino é se 62.5ns (1/16Mhz)
// A base de tempo do timer interrupt será, portanto, de aproximados 1ms: tempo = Resoluçao x Pre scaler x tempo de Ciclo de máquina = 256 * 64 * 62.5ns = 1024us 
//
// O controle do servo motor:
//
// O período típico de pulso de controle do servo é aproximadamente 20ms, que é igual a aproximados 20 cliclos de timer interrupt
// Este período não é critico. É aceitável uma variação razoável do período, mas vamos assumir uma variação máxima de 20% ou 4ms
// O Duty cycle do pulso determina o angulo de posicão do servo (modelo de ref.), variando entre 600us e 2400us, correspondendo respectivamente à 0 e 180 graus
// Assim, a cada aproximados 20ms é necessário enviar um pulso para o servo, com a duração (duty cycle) correspondente ao angulo de posição desejado.
//
// Para fazer isso implementei o metodo pulse com um contador que é chamado pela rotina de timer interrupt. como ajustamos o overflow do timer para 
// cada aproximados 1ms, temos que contar 20 chamadas do método para então gerar um pulso. Assim, incrementamos o contador a cada chamada e, quando
// ele chega em 20, produzimos o pulso de controle do serve e zeraramos o contador, reiniciando o ciclo.
//
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
